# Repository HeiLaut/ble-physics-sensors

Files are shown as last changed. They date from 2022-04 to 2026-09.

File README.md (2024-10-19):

# BLE Sensors for physics class

* [Goal](#goal)
* [Microcontroller and Sensors](#sensors)
   * [Force Sensor](#force)
   * [ToF Distance-Sensor](#tof)
   * [Light Gate](#gate)
   * [Magnetometer](#magnet)
   * [DC Multimeter](#multimeter)
   * [Barometer](#barometer) 

## Goal 

**Easy to use** and affordable sensor boxes for digital data acquisition are suitable for use in physics lessons by students or for teacher demonstrations.

Each box can be assembled for less than 20 €.

Comments and requests for changes to both the 3D files and the Arduino code are welcome.

## Microcontroller and Sensors 

All boxes are equipped with an ESP32, enabling them to communicate via BLE (Bluetooth Low Energy) or a serial connection.

I use the Wemos Lolin32Lite development board because of its availability, the battery connector and the low price.

Most sensors use the I2C interface to communicate with the ESP32.

### Force Sensor 
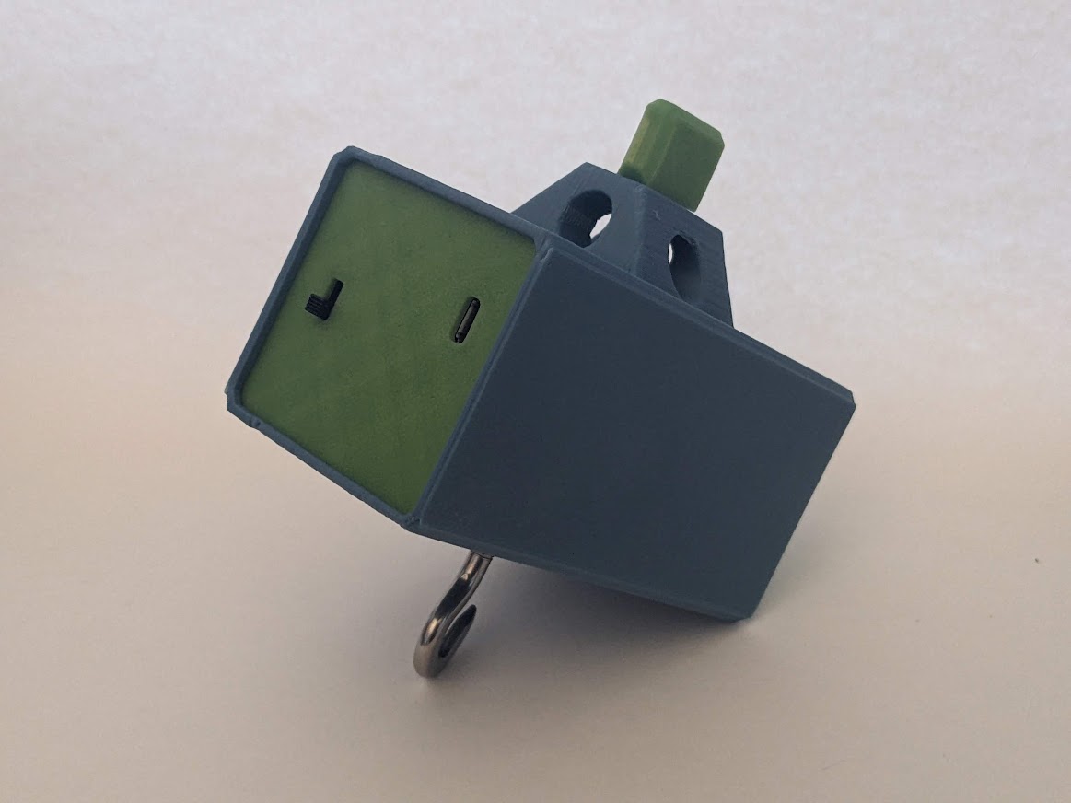
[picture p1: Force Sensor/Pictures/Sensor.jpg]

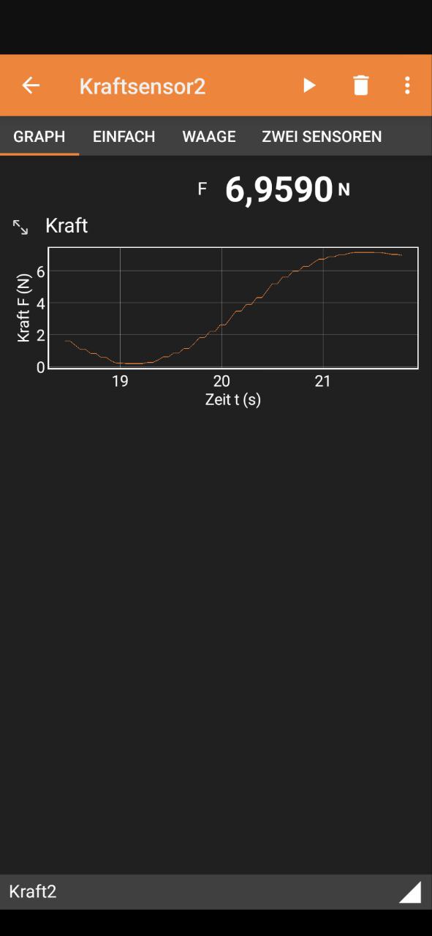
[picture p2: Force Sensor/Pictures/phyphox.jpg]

Sensor:

Load Cell and HX711 amplifier

### ToF Distance-Sensor 
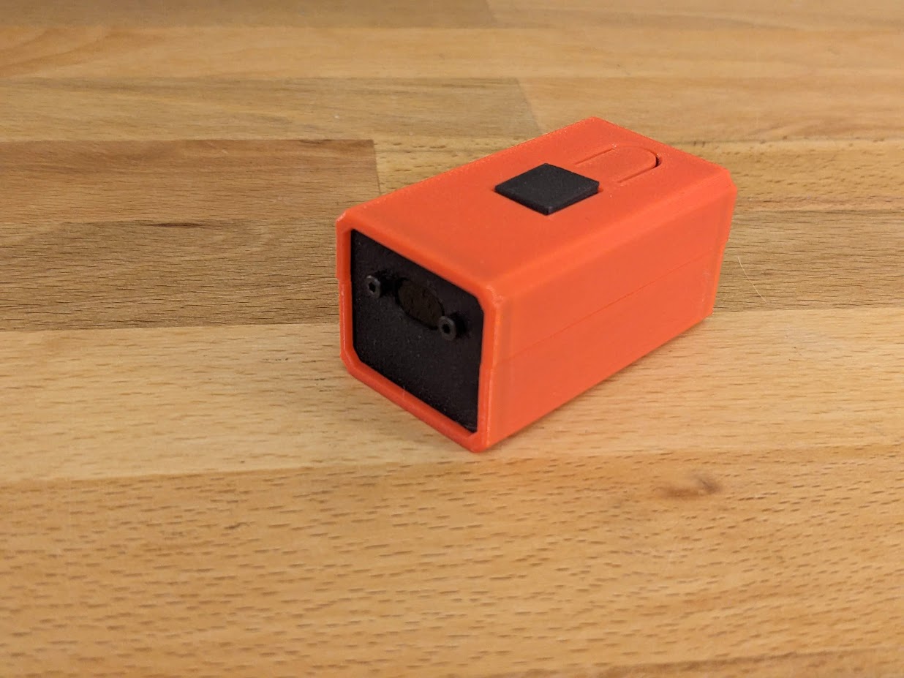
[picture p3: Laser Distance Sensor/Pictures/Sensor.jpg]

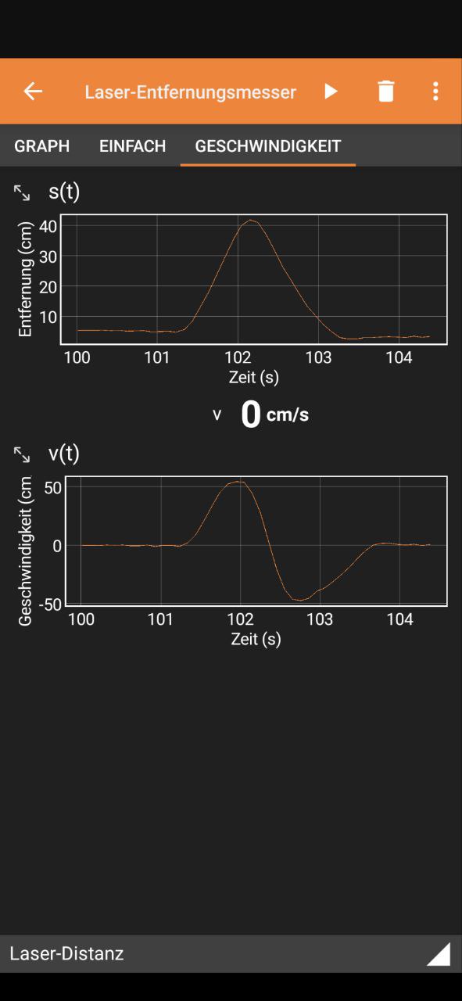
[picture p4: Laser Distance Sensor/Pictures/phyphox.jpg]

Sensor:

VL53L0X

or

VL53L1X

[Assembly instructions see wiki](https://github.com/HeiLaut/ble-physics-sensors/wiki/Laser-Distance)

### Light Gate 

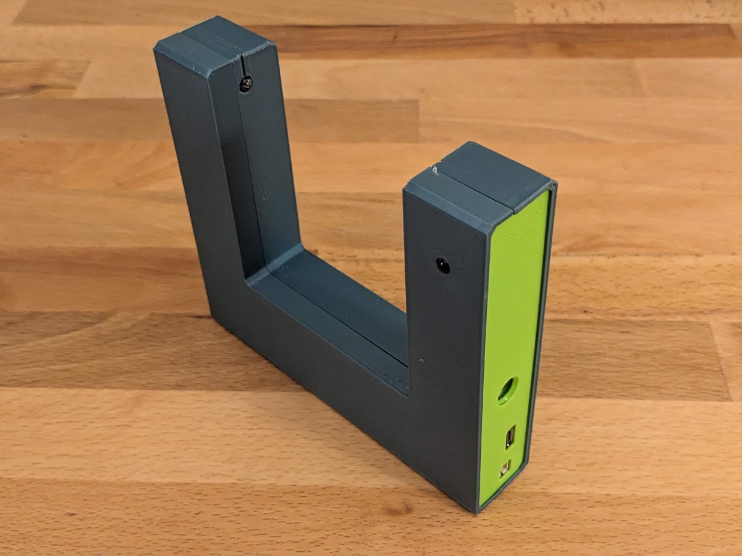
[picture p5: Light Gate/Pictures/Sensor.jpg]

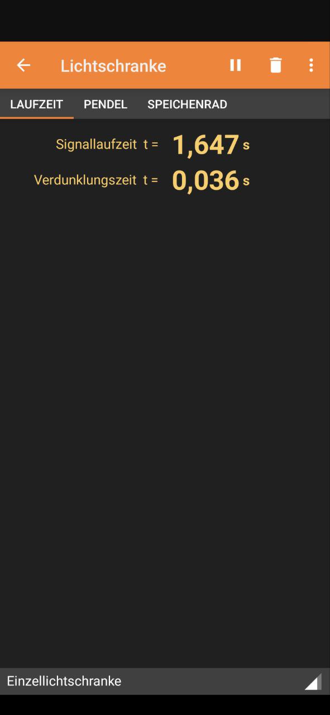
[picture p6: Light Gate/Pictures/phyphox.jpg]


Sensor:

Adafruit Break Beam Sensor 

or (cheaper)

modified lightgate/speed-sensor with LM393

### Magnetometer 
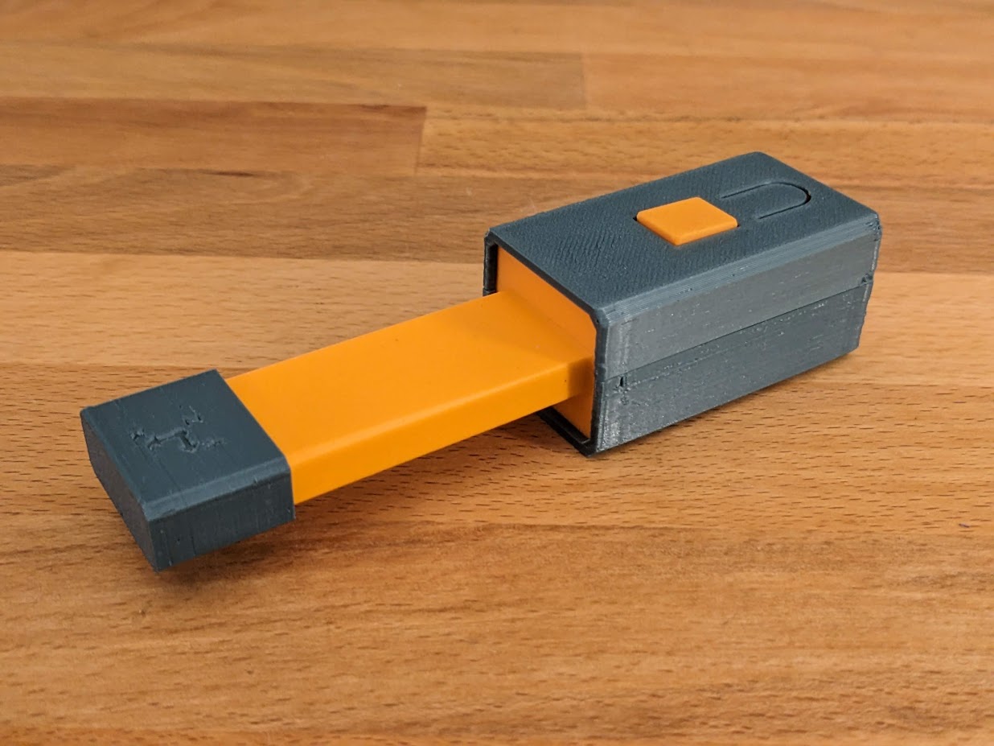
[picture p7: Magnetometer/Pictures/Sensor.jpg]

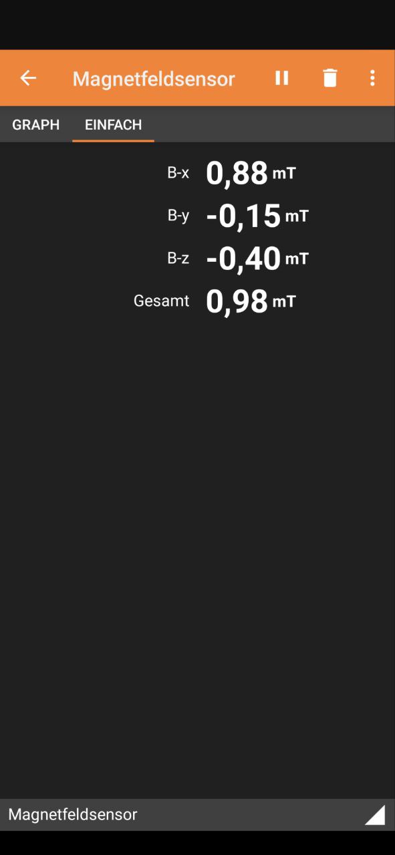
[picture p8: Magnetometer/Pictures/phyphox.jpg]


Sensor:

LIS2MDL

or

MLX90393

or

(Gy-271) low range 

### DC Multimeter 

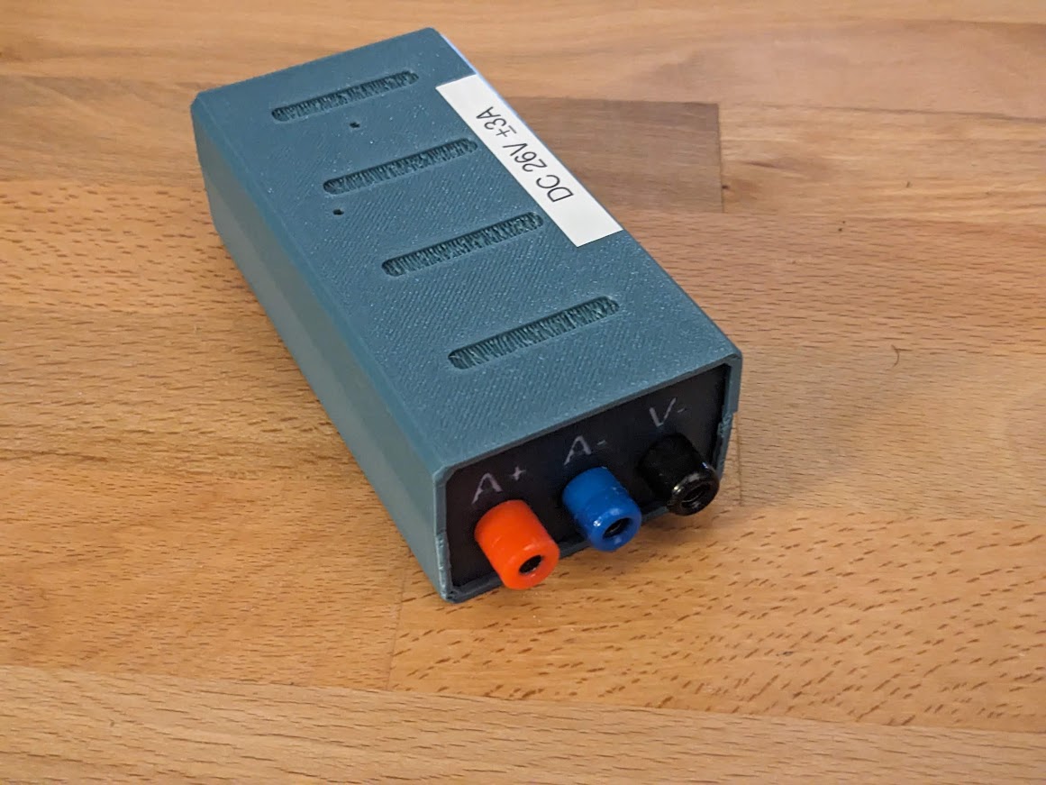
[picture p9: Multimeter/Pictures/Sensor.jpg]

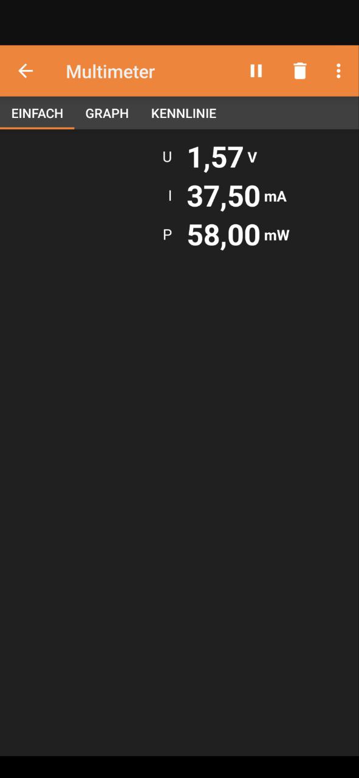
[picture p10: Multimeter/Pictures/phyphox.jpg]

Sensor:

INA219

and (optional)

ADS1115

Example Videos:

Diode characteristic https://youtu.be/DQ5L0hsJfBA

Resistor characteristic https://youtu.be/PSxBtcULFwU

Charge and discharge of a capacitor https://youtube.com/shorts/HkM0g7PQ94s?feature=share

### Barometer 
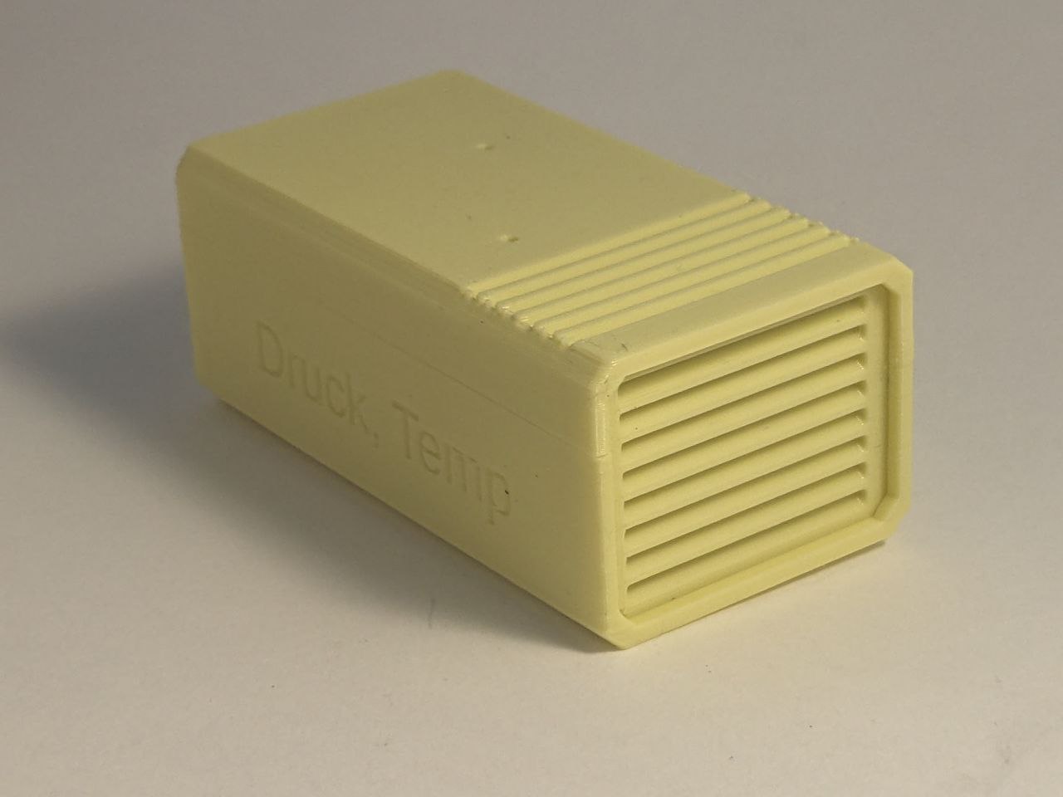
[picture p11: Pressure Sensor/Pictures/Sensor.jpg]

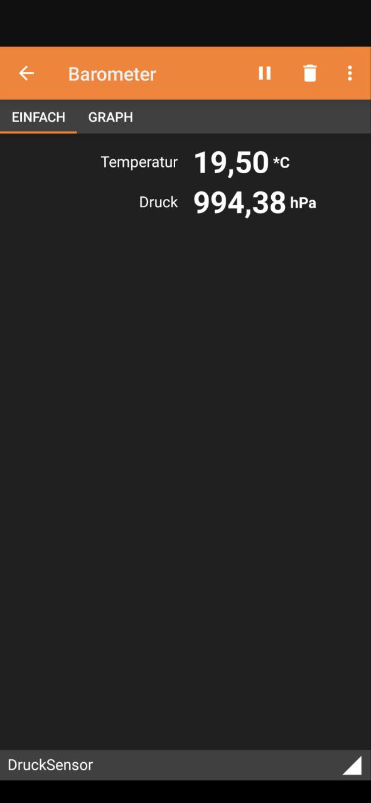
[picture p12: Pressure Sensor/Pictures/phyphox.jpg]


BMP180 Barometer and Thermometer module.

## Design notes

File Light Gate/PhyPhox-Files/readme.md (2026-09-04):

If you use the Arduino sketch, light_gate_qr you must load this experiment to phyphox ether by sharing the phyphox-file or by scanning the QR code.

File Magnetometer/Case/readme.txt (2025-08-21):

This is a case for a Lolin32 Lite and various magnetic field sensor modules.
For all sensors, you need to print:

Bottom_Case_Lolin32Lite.stl
Top_Case_Lolin32Lite.stl
Backplate.stl

Then, you can choose from different sensors.
For each sensor, you need to print:

..._sensor.stl
..._cap.stl

you can also choose the build plate for the LIS2MDL and the MLX90393

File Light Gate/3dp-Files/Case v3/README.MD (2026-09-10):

if you use a break beam sensor from aliexpress, select the break_beam_sensor_version of from the stl

if you have single IR-Emitter and IR-Receiver LEDs by using an IR-Sensor use th 00_BUILD_PLATE.stl

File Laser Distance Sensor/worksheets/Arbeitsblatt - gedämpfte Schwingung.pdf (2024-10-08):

# Gedämpte Schwingung

## Aufgabe

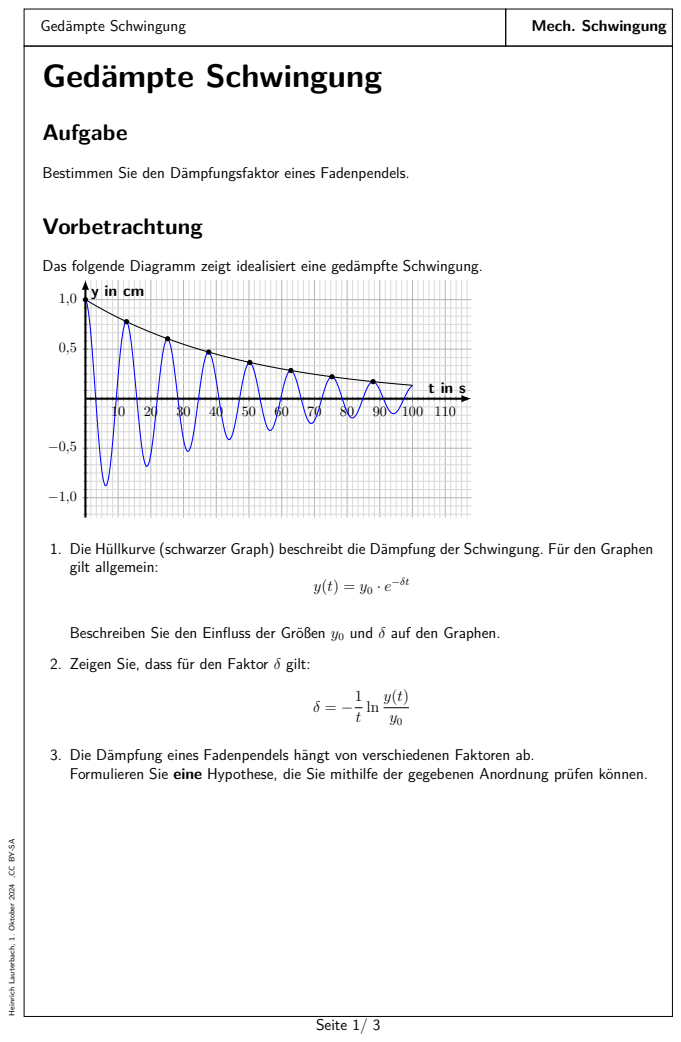
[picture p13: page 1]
Gedämpte Schwingung; Mech. Schwingung; Vorbetrachtung

Bestimmen Sie den Dämpfungsfaktor eines Fadenpendels.

Das folgende Diagramm zeigt idealisiert eine gedämpfte Schwingung.

1. Die Hüllkurve (schwarzer Graph) beschreibt die Dämpfung der Schwingung. Für den Graphen
gilt allgemein:

Beschreiben Sie den Einfluss der Größen y0 und δ auf den Graphen.

2. Zeigen Sie, dass für den Faktor δ gilt:

3. Die Dämpfung eines Fadenpendels hängt von verschiedenen Faktoren ab.
Formulieren Sie eine Hypothese, die Sie mithilfe der gegebenen Anordnung prüfen können.

Heinrich Lauterbach, 1. Oktober 2024 ,CC BY-SA

Heinrich Lauterbach, 1. Oktober 2024 ,CC BY-SA

### Durchführung

1. Hängen Sie das Pendel in Ruhelage auf und positionieren Sie den ToF-Sensor auf Höhe des Pendels.

Versuchsaufbau

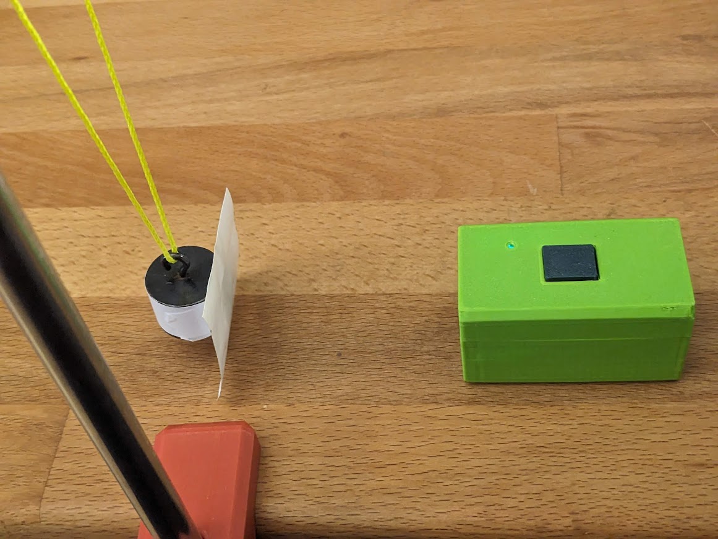
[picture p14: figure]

2. Stellen Sie mithilfe des Tasters auf dem Sensor den Offset ein, sodass der Punkt der Ruhelage auf 0 gesetzt wird.
3. Lenken Sie das Pendel um einen kleinen Winkel aus und starten Sie die Messung mit phyphox.
4. Speichern Sie die Messung auf Ihrem Gerät. (Öffnen Sie das Menü hinter den drei Punkten und klicken Sie auf Zustand speichern.)
5. Wiederholen Sie die Messung, variieren Sie vorher eine Größe entsprechend Ihrer Hypothese.

### Auswertung

1. Entnehmen Sie aus den y(t)-Diagrammen in phyphox jeweils mindestens fünf Amplituden in Abhängigkeit von der Zeit. Vergrößern Sie dazu das s(t)-Diagramm und wählen Sie mithilfe des Cursors die entsprechenden Amplituden aus.
Da die Zeit nicht bei 0 s anfängt, ziehen Sie jeweils den Startwert der Zeit von Ihren abgelesenen Werten ab, sodass die erste Auslenkung bei t = 0 ist.
2. Ermitteln Sie mithilfe der Messwerte die Dämpfungsfaktoren δ der jeweiligen Schwingung.
3. Überprüfen Sie unter Beachtung möglicher aufgetretener Messunsicherheiten Ihre Hypothese.

Heinrich Lauterbach, 1. Oktober 2024 ,CC BY-SA

## Hinweise und Erwartung

Beispielgraph

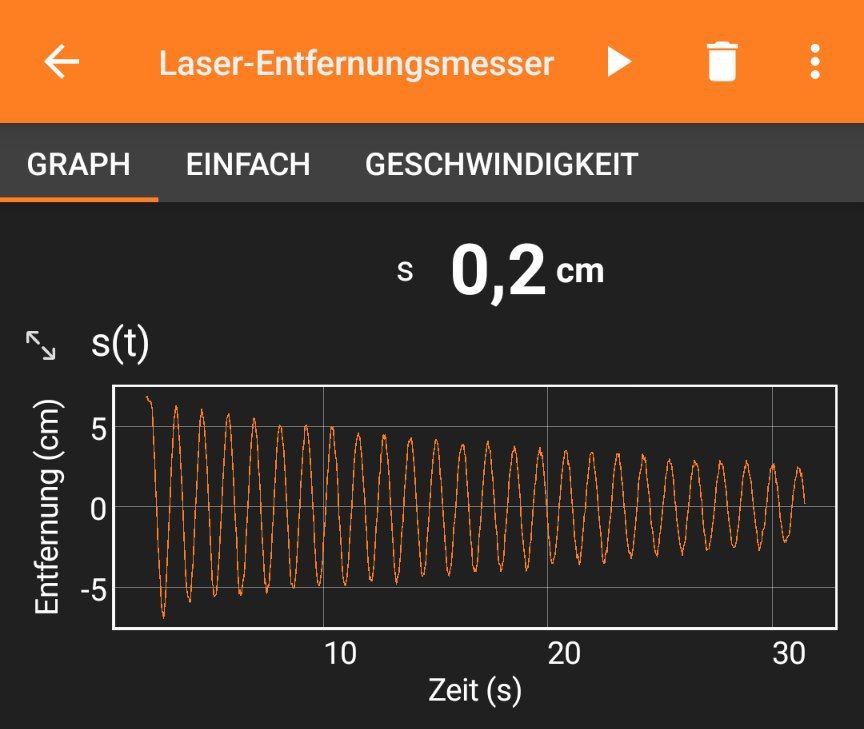
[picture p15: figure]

Beispielmesswerte in unterschiedlichen Abständen
t in s | ti
| in s | y in cm | δ
2,90 | 0 | 6,9 | –
6,33 | 3,43 | 5,5 | 0,066
9,82 | 6,92 | 4,9 | 0,049
14,41 | 11,51 | 4,3 | 0,041
23,71 | 20,81 | 3,2 | 0,037
30,52 | 27,62 | 2,2 | 0,041

δ = 0, 047

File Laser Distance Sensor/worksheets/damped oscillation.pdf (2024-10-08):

# Damped Oscillation

## Task

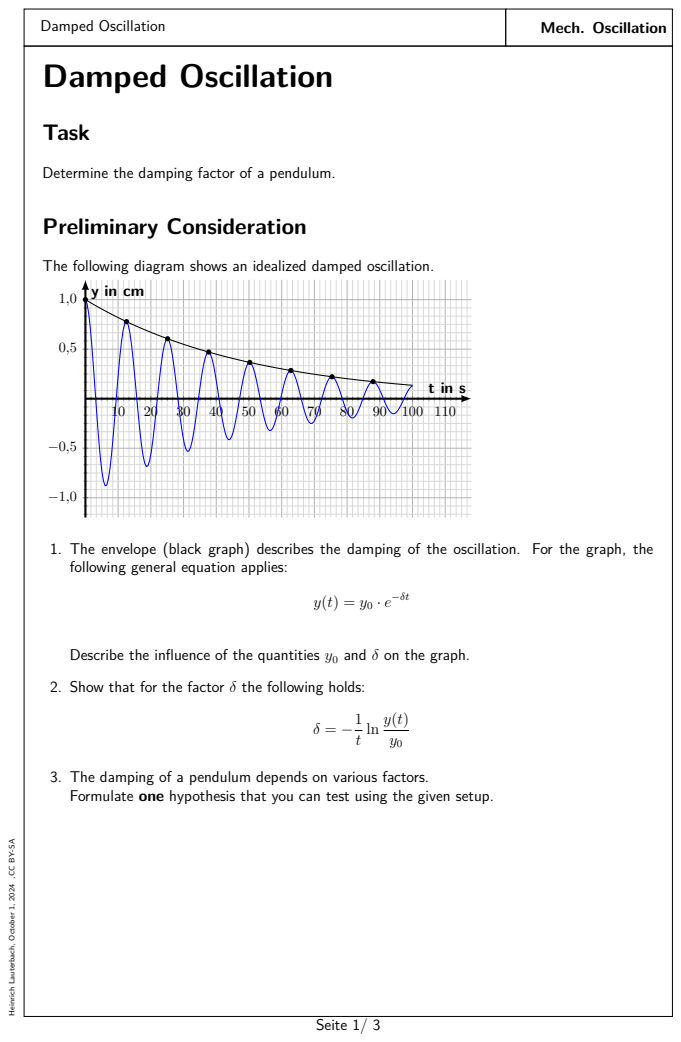
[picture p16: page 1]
Damped Oscillation; Mech. Oscillation; Preliminary Consideration

Determine the damping factor of a pendulum.

The following diagram shows an idealized damped oscillation.

1. The envelope (black graph) describes the damping of the oscillation. For the graph, the
following general equation applies:

Describe the influence of the quantities y0 and δ on the graph.

2. Show that for the factor δ the following holds:

3. The damping of a pendulum depends on various factors.
Formulate one hypothesis that you can test using the given setup.

Heinrich Lauterbach, October 1, 2024 ,CC BY-SA

Heinrich Lauterbach, October 1, 2024 ,CC BY-SA

### Procedure

1. Hang the pendulum in its rest position and position the ToF sensor at the height of the pendulum.

Experimental Setup


2. Use the button on the sensor to set the offset so that the point of rest is set to 0.
3. Displace the pendulum by a small angle and start the measurement with phyphox.
4. Save the measurement on your device. (Open the menu behind the three dots and click on Save State.)
5. Repeat the measurement, varying one parameter according to your hypothesis.

### Evaluation

1. Extract at least five amplitudes as a function of time from the y(t) diagrams in phyphox. To do this, enlarge the s(t) diagram and use the cursor to select the corresponding amplitudes. Since the time does not start at 0 s, subtract the start value of the time from your read values so that the first displacement is at t = 0.
2. Determine the damping factors δ of the respective oscillation using the measured values.
3. Verify your hypothesis, considering possible measurement uncertainties.

Heinrich Lauterbach, October 1, 2024 ,CC BY-SA

## Notes and Expectations

Example Graph


Example Measurements at Different Intervals
t in s | ti
| in s | y in cm | δ
2.90 | 0 | 6.9 | –
6.33 | 3.43 | 5.5 | 0.066
9.82 | 6.92 | 4.9 | 0.049
14.41 | 11.51 | 4.3 | 0.041
23.71 | 20.81 | 3.2 | 0.037
30.52 | 27.62 | 2.2 | 0.041

δ = 0.047

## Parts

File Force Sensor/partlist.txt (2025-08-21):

esp32 lolin lite
1kg load cell with hx711

2 m4x20 screws
2 m4 nuts
1 m5 hook
2 m5x14 screws
12 x 12 x 7.3 mm tactile push button

optional:
SS-12F15 on/off-switch
lipo battery

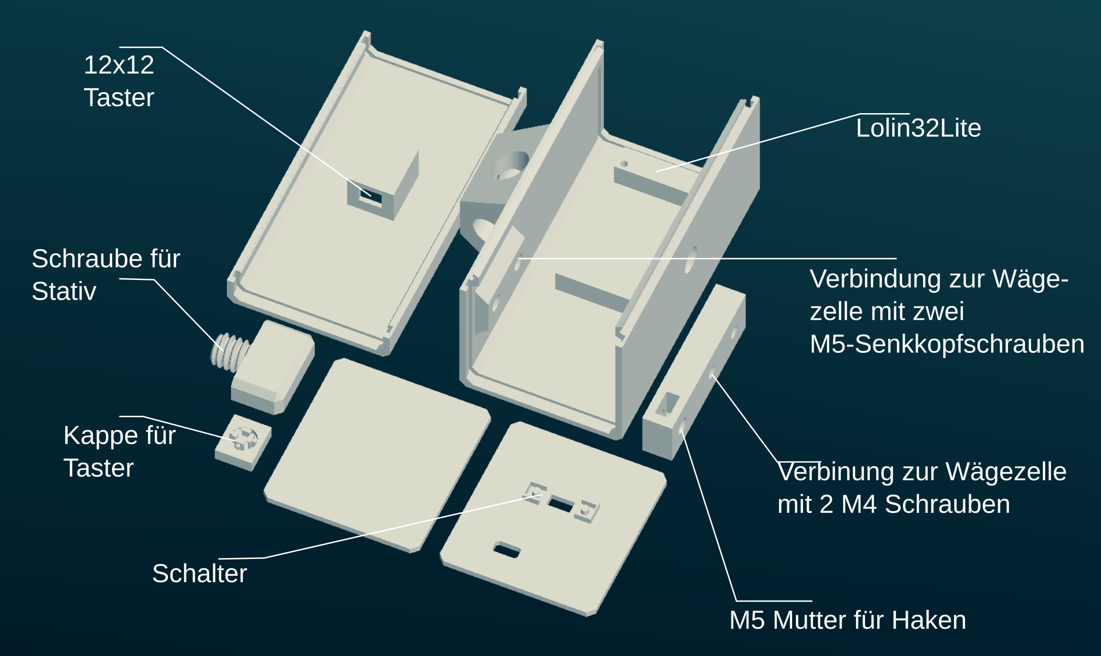
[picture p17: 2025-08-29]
Force Sensor/Pictures/parts_de.png

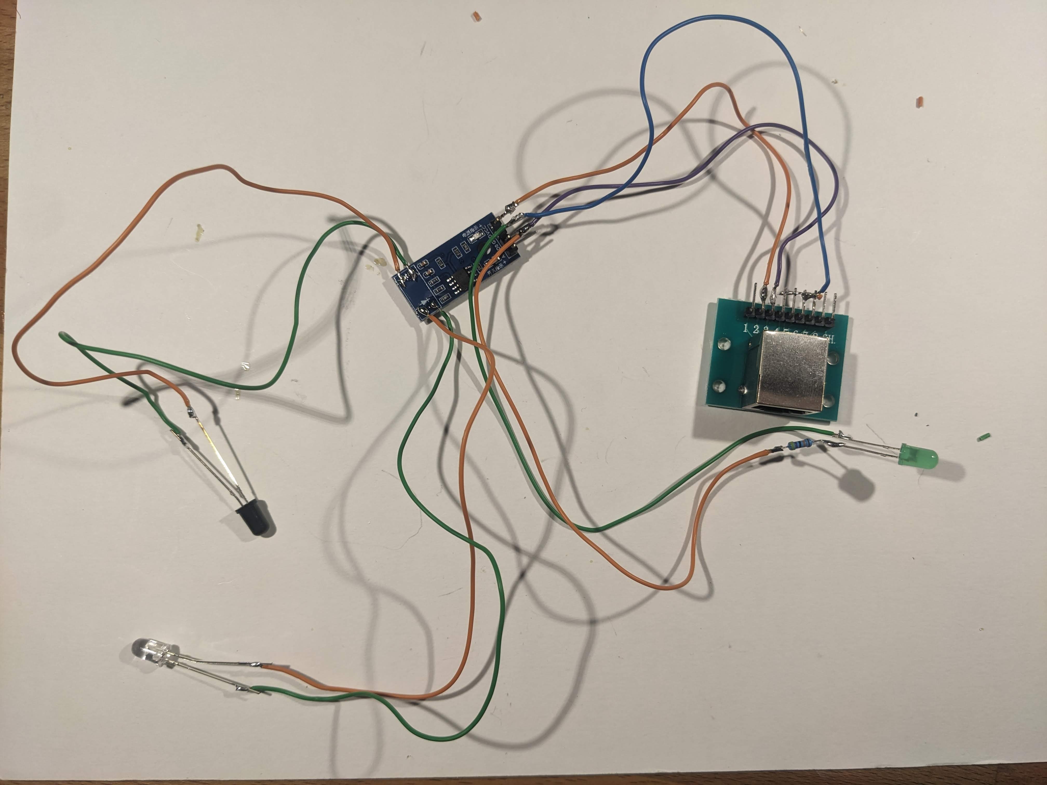
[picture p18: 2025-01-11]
Light Gate/Pictures/Instructions/parts_2nd_lightgate.jpg

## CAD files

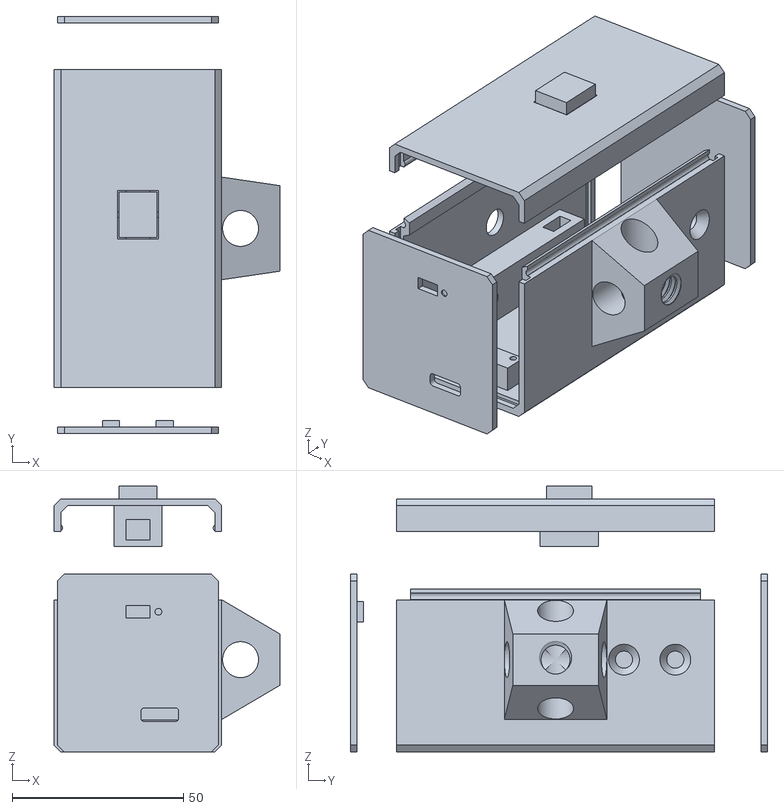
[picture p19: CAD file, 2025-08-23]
Force Sensor/3dp-Files/case_assembly.stl
66.0 x 122.0 x 77.8

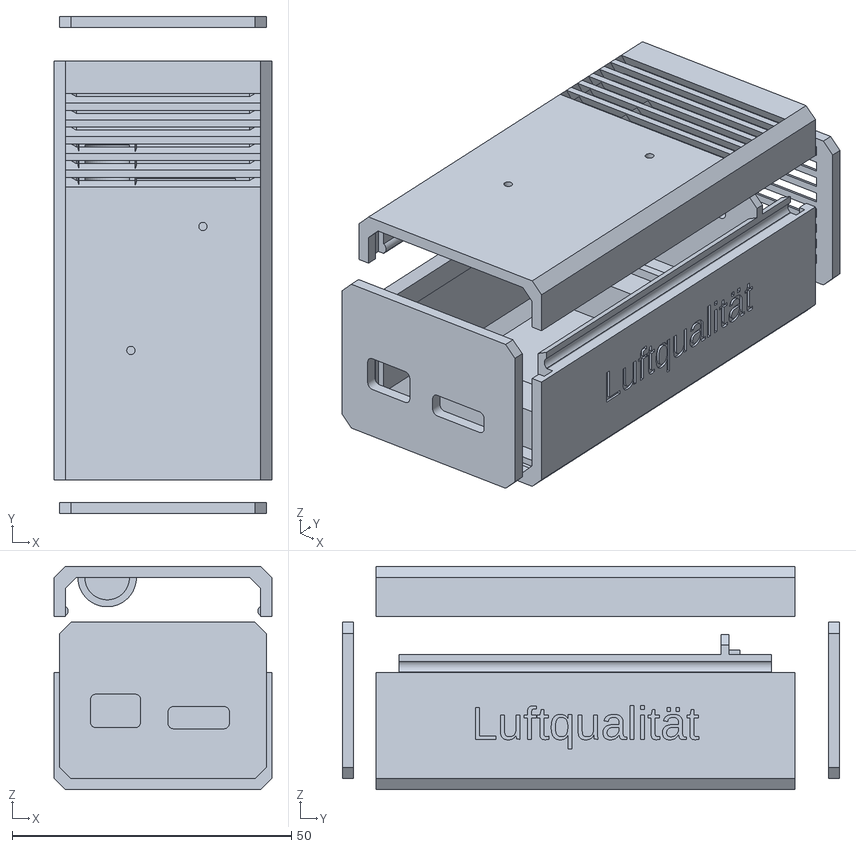
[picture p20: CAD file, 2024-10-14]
Airquality/3dp/AirQualityCase.stl
39.0 x 89.0 x 40.0

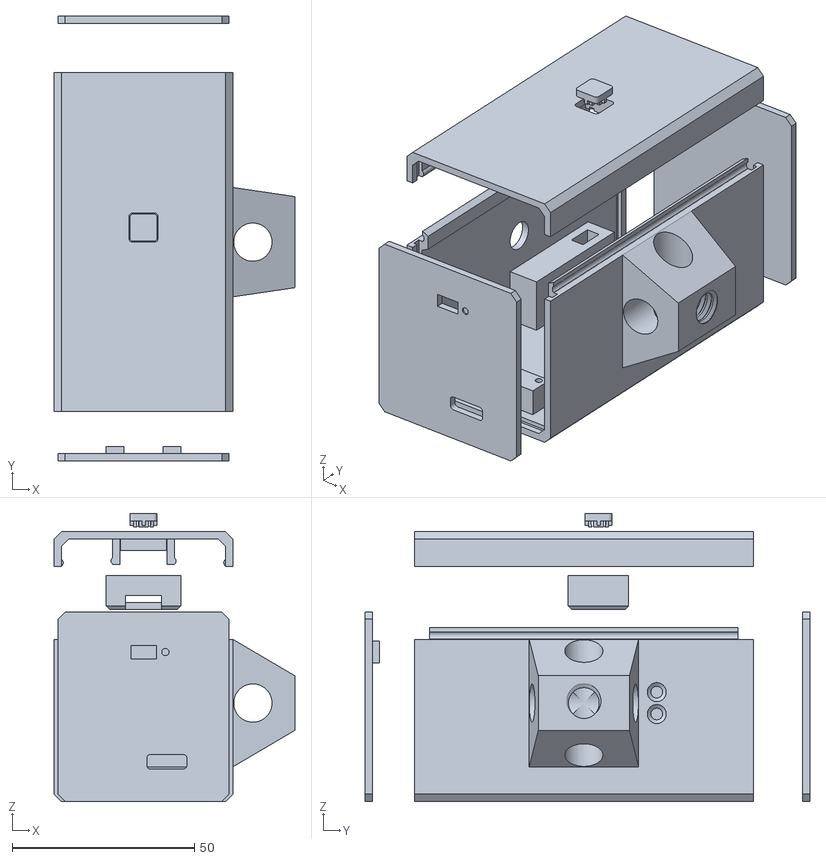
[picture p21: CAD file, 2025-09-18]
Force Sensor/3dp-Files/case_v5_100g_LoadCell.stl
66.0 x 122.0 x 79.0

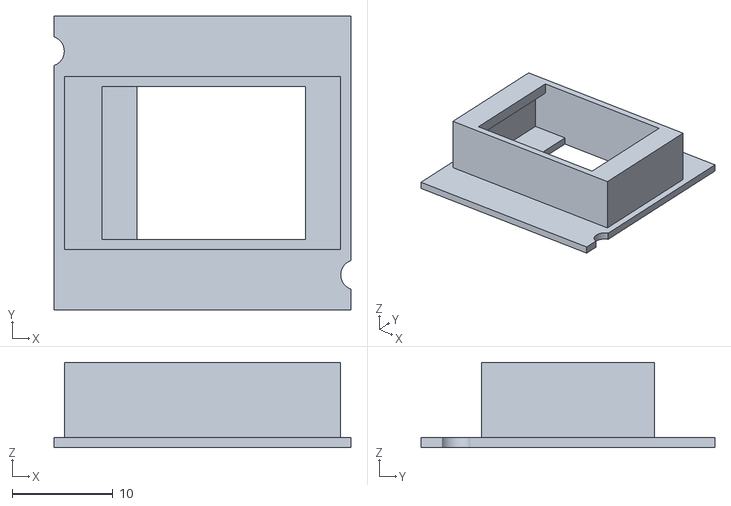
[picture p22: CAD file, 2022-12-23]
Force Sensor/3dp-Files/parts/rj45-blende-edit.stl
29.5 x 29.2 x 8.50

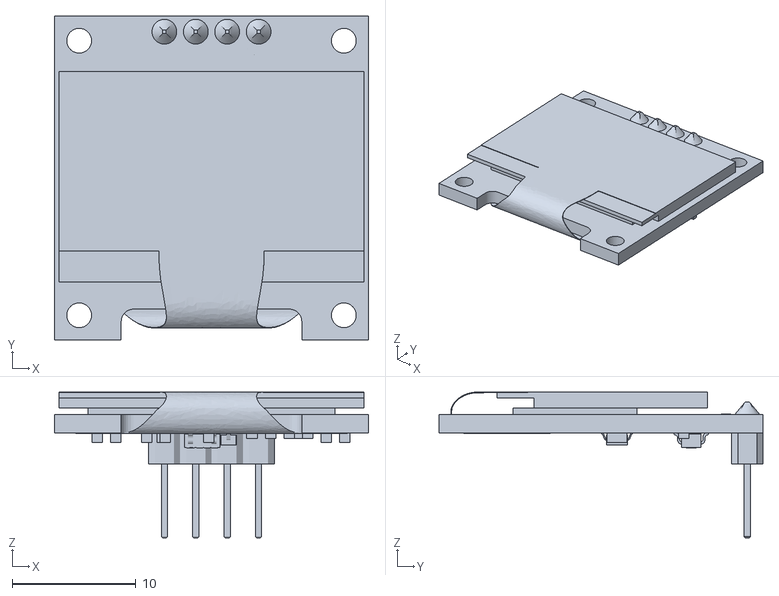
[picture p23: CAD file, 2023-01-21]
Infrared Reflection Sensor/3dp-Files/parts/OLED.stl
25.4 x 26.2 x 11.8

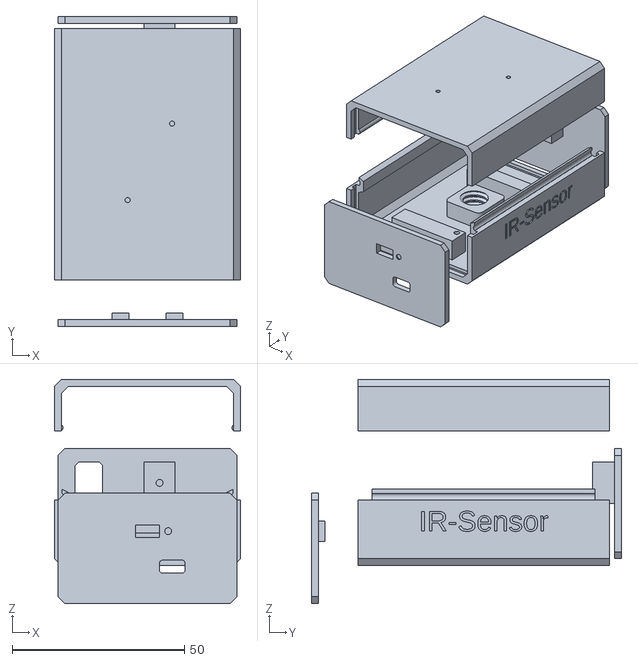
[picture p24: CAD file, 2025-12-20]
Infrared Reflection Sensor/3dp-Files/TR5000Case.stl
54.0 x 90.0 x 65.0

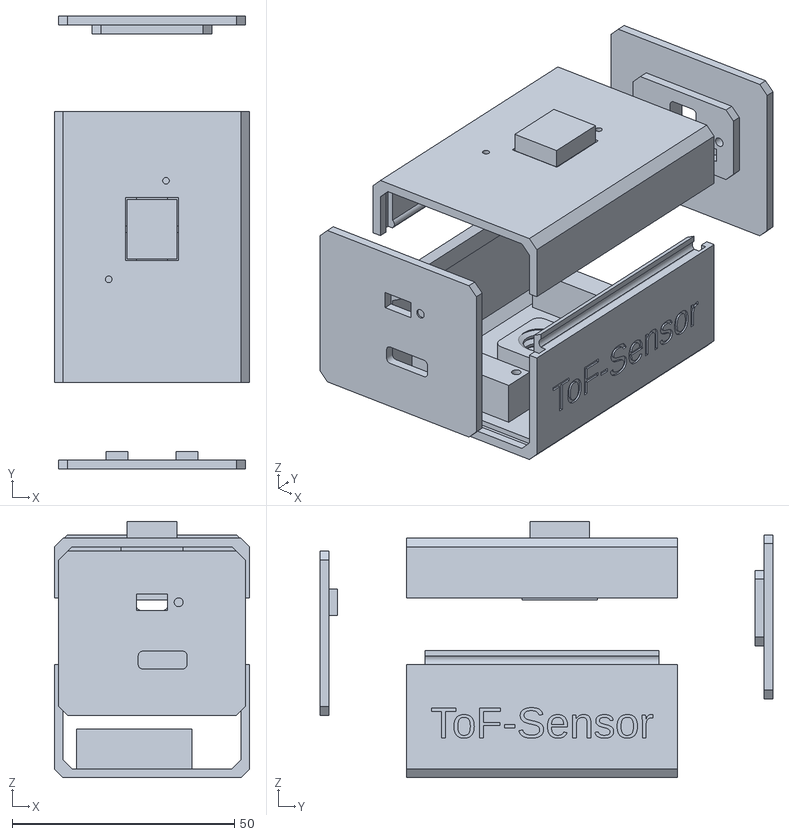
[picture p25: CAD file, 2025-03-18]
Laser Distance Sensor/3dp-Files/Case v2/vl53l0x_case2.stl
44.0 x 102.0 x 57.8

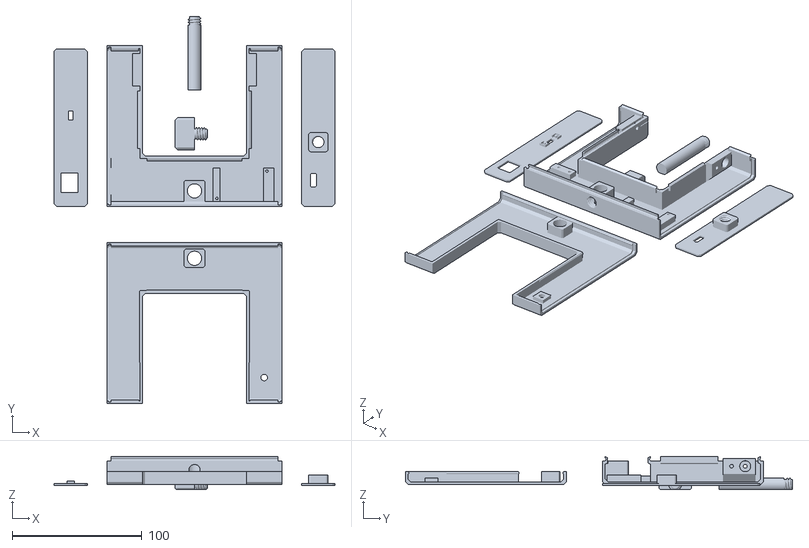
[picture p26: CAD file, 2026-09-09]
Light Gate/3dp-Files/Case v3/break_beam_sensor_version_build_plate.stl
216.6 x 298.5 x 25.5

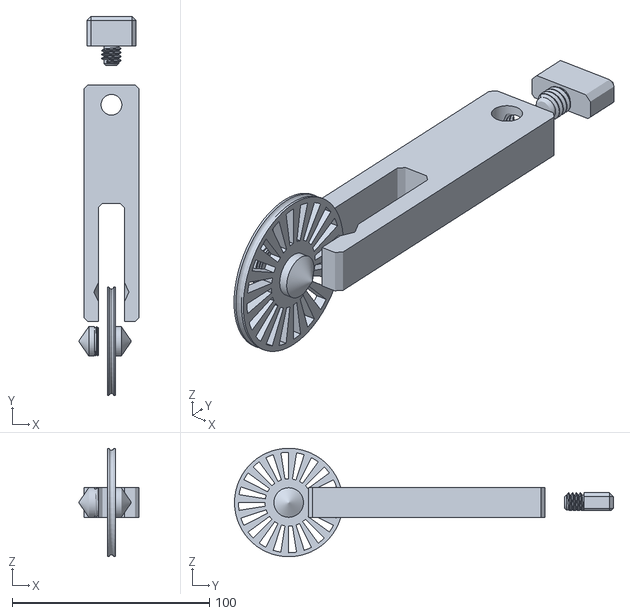
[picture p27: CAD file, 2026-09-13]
Light Gate/3dp-Files/Case v3/Encoder-Wheel/Encoder_Wheel_3d_only.stl
30.5 x 192.3 x 55.0

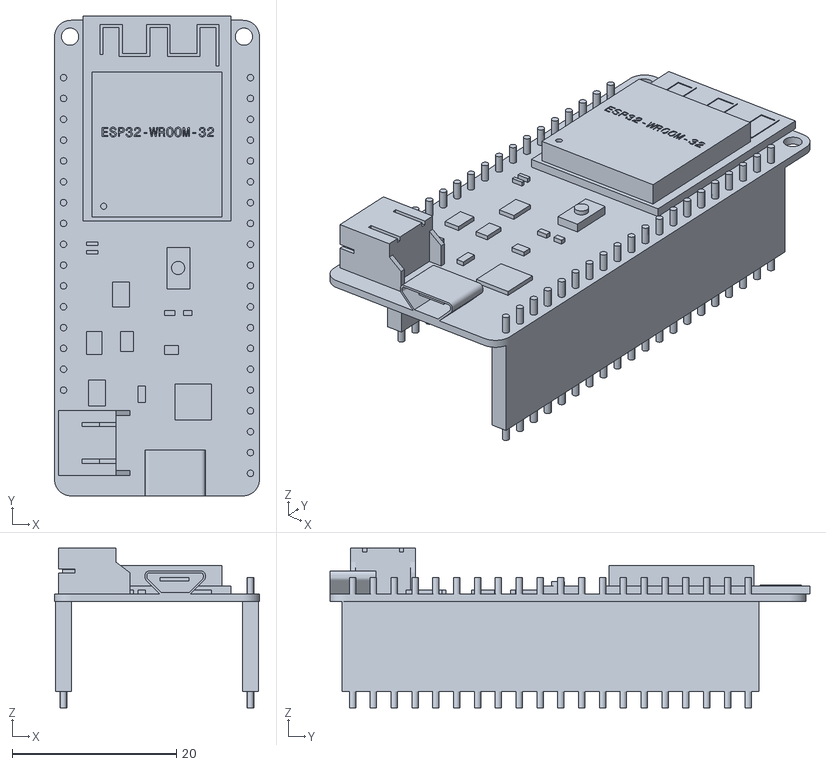
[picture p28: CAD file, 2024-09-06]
Light Gate/3dp-Files/Case v3/parts/Wemos-Lolin32.stl
25.0 x 58.5 x 19.5

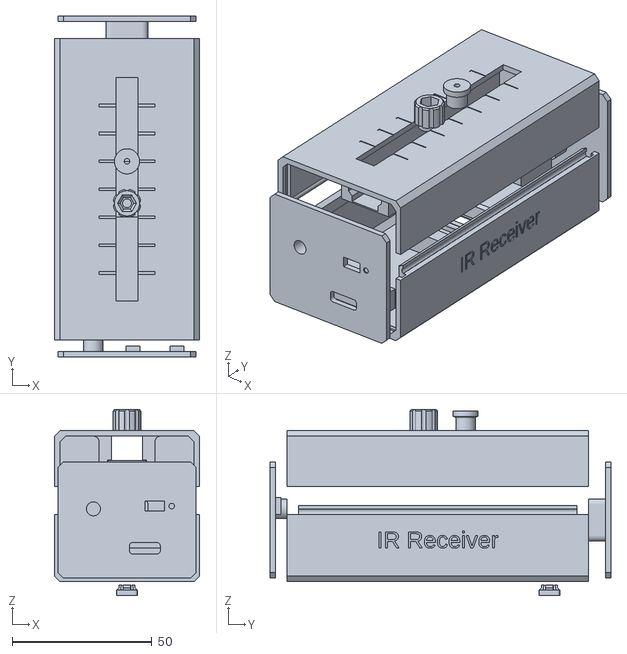
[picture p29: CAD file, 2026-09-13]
Light Gate/3dp-Files/receiver emitter seperate/Receiver_case_all_parts.stl
52.0 x 122.0 x 66.5

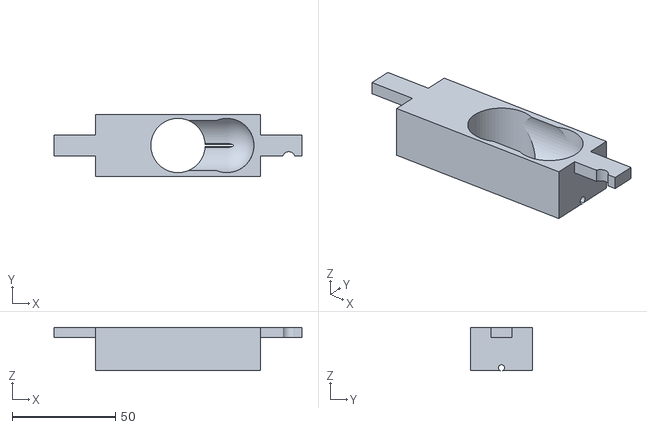
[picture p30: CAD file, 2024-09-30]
Light Gate/3dp-Files/Startvorrichtung/Kugelstarter25_3.stl
120.0 x 30.0 x 21.0

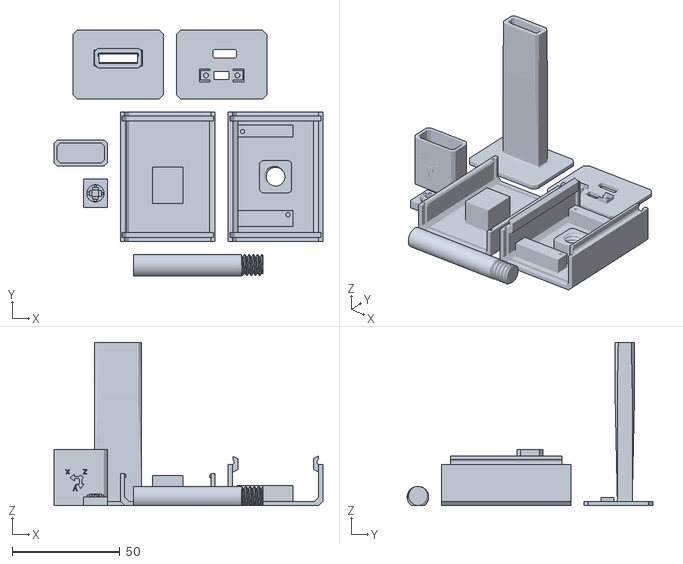
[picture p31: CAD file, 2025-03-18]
Magnetometer/Case/lis2mdl_build_plate.stl
124.8 x 114.0 x 75.8

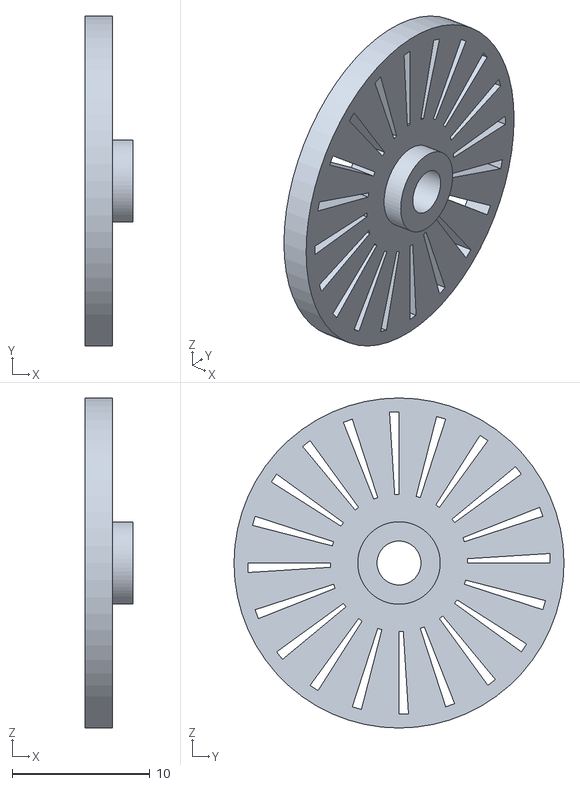
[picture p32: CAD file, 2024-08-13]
Messwagen/3dp-Files/Encoder_Wheel.stl
3.50 x 24.0 x 24.0

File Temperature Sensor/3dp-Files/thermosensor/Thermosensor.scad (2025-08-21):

include <BOSL/constants.scad>
use <BOSL/transforms.scad>
use <BOSL/shapes.scad>
use <BOSL/masks.scad>

$fn = 60;
x= 52;
z = 23;
y = 30+28;



module esp(){
   color("red")translate([1.5,42.5,0])rotate([180,0,-90])import("/parts/lolin32_lite.stl");
}

module connectorboard(){
   xB = 38;
   yB = 30;
   zB = 1.5;
   cuboid([xB,yB,zB]);
   color("blue")translate([0,yB/2-5,zB-0.5]){
   translate([xB/2-8.5,0,0])import("/parts/jst.stl");
   translate([xB/2-26,0,0])import("/parts/jst.stl");
   }


}
module parts(){
   translate([-38/2,30/2+1,0.75])connectorboard();
   translate([0.5,-25,0])rotate([0,1,0])rotate([0,0,90])esp();
}

module case(){
   module screwshaft(){
        difference(){
            cylinder(d=4,h=z-3);
            up(15)cylinder(d=2,h=z);
            up(5)rotate([0,-50,0])cuboid([20,10,10]);
        }
    }
    for(i=[ [-x/2+1.7,-y/2+1.7,-z/2+3.7],
            [-x/2+1.7,y/2-1.7,-z/2+3.7]]){
        translate(i)screwshaft();
    }
    mirror([1,0,0])for(i=[ [-x/2+1.7,-y/2+1.7,-z/2+3.7],
            [-x/2+1.7,y/2-1.7,-z/2+3.7]]){
        translate(i)screwshaft();
    }
   module lolinmount(){
       d = 2;
       h = 6.5;
       translate([-x/2+5,-y/2+13.7,-z/2+h/2])difference(){
            cuboid([5,26,h]);
            translate([-0.75,1-11.2,-2])cylinder(d=d,h=h);
      }
      translate([x/2-8.5,-y/2+13.7,-z/2+h/2])difference(){
            cuboid([5,26,h]);
            translate([-0.75,11,-2])cylinder(d=d,h=h);
      }
   }
   module conmount(){
      h = 6;
      translate([x/2-35/2-2,25/2,-z/2+h/2])difference(){
         cuboid([37,25,h]);
         translate([0,3,-0.2])cuboid([35-6,25,h+1]);
      }
     
   }
       
        
   difference(){
      cuboid([x+3,y+3,z+1.5],chamfer =2,edges = EDGES_Z_ALL);
      translate([0,0,0.75])cuboid([x,y,z+1],chamfer =2,edges = EDGES_Z_ALL);
      //JST
      translate([16.54,y/2+1,-1])cuboid([11,3,8]);
      translate([-1,y/2+1,-1])cuboid([11,3,8]);
      //esp
      translate([x/2+1,-23,-1.5])cuboid([3,10,8.5]);
      translate([x/2+1,-7.5,-2.5])cuboid([3,9,5]);
     }
    translate([0.5,0.5,0])lolinmount();
    conmount();
   }
   
module lid(){
   difference(){
         cuboid([x+3,y+3,1.5],chamfer =2,edges = EDGES_Z_ALL);
       for(i=[ [-x/2+1.7,-y/2+1.7,-z/2+3.7],
            [-x/2+1.7,y/2-1.7,-z/2+3.7]]){
        translate(i)cylinder(d=2,h=z);
    }
    mirror([1,0,0])for(i=[ [-x/2+1.7,-y/2+1.7,-z/2+3.7],
            [-x/2+1.7,y/2-1.7,-z/2+3.7]]){
        translate(i)cylinder(d=2,h=z);
    }
}
}
difference(){
   union(){
      case();
      translate([0,0,z/2+10])lid();
      *translate([x/2-1,-2.5,-5])parts();
   }
   //translate([0,-50,-50])cube([100,100,100]);
}

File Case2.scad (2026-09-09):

/*
  Universal Electronic Case
  
  Version: 0.41 //July 2026
  
  Created by: Heinrich Lauterbach
  License: CC-BY-SA
  This file is licensed under the Creative Commons Attribution-ShareAlike 4.0 International License.
  To view a copy of this license, visit http://creativecommons.org/licenses/by-sa/4.0/
  
  needs BOSL2 library
  download BOSL2 to your libraries folder via: https://github.com/BelfrySCAD/BOSL2
*/





include<BOSL2/std.scad>
include<BOSL2/threading.scad>



$fn = 50;
/*intersection(){
    test();
    translate([0,-30,-10])cuboid([30,20,20]);
    }
*/
module test(){
lolinspace = 5;
z = 30;
x=80;
y=70;
case([x,y,z],part="bottom",explode = 25,rd=2,lolinspace = lolinspace,button = 0,reset = 0, thread = 0,clearance = 0.2,embosstext = "TEST");
*case([x,y,z],part="top",explode = 50,rd=2,lolinspace = lolinspace,button = 1,reset = 0, thread = true,usbC = 1, wall=2,jst = 1,switch=1,charge_view = 1,
   power_view = 1);
*color("red")translate([-11.5,16.5,lolinspace-12])rotate([180,0,-90])import("lolin32_lite.stl");
}
////must be larger than 1.5 mm
module case(
   size = [15,15,15], //size [x,y,z]
   clearance = 0.15, //overall clearance,
   plate_clearance = 0,//makes the plate smaller, if the print of the large parts gets a bit loose, while printing
   wall = 2, //wall thickness
   rd = 2, //chamfer radius
   cutheight = 2, //offset of cutheight
   snap = 2, //width of snap 
   part = "all",//top, bottom, plate
   explode = 0, //show parts seperate
   lolin32lite = true, //lolin32lite mount
   lolinspace = 7.4, //spacing of lolin32lite aboce bottom part
   lolinsnap = 1,
   thread = false, //add thread on bottom part for rod
   button = false,//add buttonhole on top part
   reset = false, //add reset button
   usb = false, //add cutout for micro usb on plate
   usbC = false,//add cutout for usb-c on plate
   jst = false,//add cutout for jst (battery)
   lolinx = 0,//x-offset of lolin32lite
   charge_view = 0,//add hole on top to see charging-LED
   power_view = 0,//add hole on top to see power-LED
   buttonpos = [0,4],//position of button in top part [x,y]
   switch = 0, //mounting for on-off-switch in plate
   switchpos = [0,5],//switch postion [y,z]
   switchrot = 0,//rotation of switch in degree
   embosstext = "",//embosstext on bottom part
   embossrot = [90,0,90],
   embossheight = 0.4,//embossheight means depth
   embosspos = [0,-5]
   )
   {
   x = size[0];
   y = size[1];
   z = size[2];
   embosspos = [x/2+2-0.2,embosspos[0],embosspos[1]];


   ox = x+2*wall;
   oy = y+4*wall;
   oz = z+2*wall;
   // select chamfer OR rounding
   //chamfer = 1;
   //rounding = 1;

   //rd = 2;

   clearance = clearance;

   //overlap of front and back plate into body
   overlap = 1;

   //height of cut between upper and lower half. 0 means in the middle <1 upper half bigger than lower half; >1 lower half bigger than upper half
   //cutheight = snap;

   //snap parts
   d1 = snap;

   if(cutheight>z/2-wall){
      echo("Cuthehgt to large");
   }
   module body(explode = 2,part){
         module both(){
            difference(){
            cuboid([ox,oy,oz],chamfer = rd,except=[FRONT,BACK]);
            cuboid([x,oy+1,z],chamfer = rd,except=[FRONT,BACK]);
            for(i = [-1,1]){
               translate([0,i*(-y/2-wall/2),0])cuboid([x+2*overlap+clearance*2,wall+clearance*2,z+2*overlap+clearance*2],chamfer = rd,except=[FRONT,BACK]);
               }//end for
            }//end difference
            }//end both
            
          //top part of the case
         module upper(){
            difference(){
               both();
               translate([0,0,cutheight])cuboid(x*y,anchor=TOP);
               if(button){
                  translate([buttonpos[0],buttonpos[1],z/2])rotate([180,0,90])buttonCase2("cutout",wall);
                  }
               //reset button
               if(reset){
                  translate([-0.8,-y/2+5,z/2+0.1])difference(){
                     union(){
                        cyl(d=10,h=4);
                        cuboid([10,10,4],anchor=FRONT);
                        }//end union
                       cyl(d=8.5,h=4);
                       cuboid([8.5,10,4],anchor=FRONT);
                     }//end difference
                     translate([-0.8,-y/2+5,z/2-1])union(){
                        cyl(d=10,h=4);
                        cuboid([10,10,4],anchor=FRONT);
                  }//end union
                  //LED-cutouts
                

                  }//end if reset
                  if(charge_view)translate([-5.75+lolinx,-6.8-y/2+52/2,z/2])cyl(d=1.5,h=10);
                  if(power_view)translate([7.15+lolinx,15.4-y/2+52/2,z/2])cyl(d=1.5,h=10);
            }//end difference
            
            //snap connector male
            for(i = [-1,1]){
               translate([i*(-x/2-d1/4),0,cutheight+d1/2])difference(){
                  ycyl(d = d1, h = y-clearance*2);
                  translate([-i*d1/4,0,0])cuboid([3*d1/4,y-clearance*2,d1]);
                  }
               }//end for
            if(button){
               translate([buttonpos[0],buttonpos[1],z/2])rotate([180,0,90]){
               buttonCase2("snap");
               up(10)buttonCase2("cover");
               down(5)buttonCase2("cap");

               }
               }
            if(reset){
                translate([-0.8,-y/2+3.5,z/2+1])cyl(d=3,h=z-lolinspace-2.6,anchor=TOP);

            }
         }//end uppercase
         
         //lower part of the case
         module lower(){
            difference(){
               both();
               translate([0,0,cutheight])cuboid(x*y,anchor=BOTTOM);
               if(button){
                  #translate([buttonpos[0],buttonpos[1],-z/2])rotate([0,0,90])buttonCase2("cutout",wall);
                  }
               if(thread){
                  translate([0,0,-z/2])cuboid([13,13,15],rounding=2,except=[TOP,BOTTOM]);
               }//end if thread
               //embosstext
               if(embosstext!="")translate(embosspos)rotate(embossrot)text3d(embosstext,size=6,h=embossheight,anchor=CENTER);
            }//end difference
            //snap connector female
            for(i=[-1,1]){
               difference(){
                  translate([i*(x/2),0,cutheight+d1/8])rotate([0,i*90,0])prismoid(size1=[d1*2,y-clearance*2], size2=[d1*3,y-clearance*2], h=d1,anchor=TOP);
                  translate([i*(x/2+d1/4),0,cutheight+d1/2])ycyl(d = d1+clearance*2, h = y-clearance*2);
                  translate([i*(x/2-clearance/2),0,cutheight])cuboid([clearance,y,d1*4/2],anchor = BOTTOM);
                  }//end difference
               }//end for
               if(button){
               translate([buttonpos[0],buttonpos[1],-z/2])rotate([0,0,90]){
               buttonCase2("snap");
               up(10)buttonCase2("cover");
               down(5)buttonCase2("cap");

               }
               }
              if(lolin32lite){
                  translate([lolinx,-(y-52)/2,0])difference(){
                     union(){
                        translate([0,-23,-z/2])cuboid([25,7.3,lolinspace],anchor = BOTTOM+FRONT);
                        translate([0,24,-z/2])cuboid([26,5.5,lolinspace],anchor = BOTTOM+BACK);
                        if(lolinsnap){
                            for(i=[-1,1])translate([i*13.3,-24.5,-z/2])cuboid([1.2,10,lolinspace+1.7],anchor =BOTTOM+FRONT)
                                attach(TOP)ycyl(d=2,h=10 );
                        }//end if lolinsnap
                     }//end union
                  translate([10.8,-17.6,-z/2])cyl(d=2,h=lolinspace+1,anchor = BOTTOM);
                  translate([-10.3,21,-z/2])cyl(d=2,h=lolinspace+1,anchor = BOTTOM);
                 }//end difference
               }//end if lolin32lite
               
               //threadmount
               if(thread){
                  translate([0,0,-z/2-wall])rodmount();
               }//end if thread
         }//end lowercase
         if(part == "upper"){
            up(explode/2)upper();
            }else{
            down(explode/2)lower();
            }
         
         
   }//end body
   module frontplate(plate_clearance=plate_clearance){
      cuboid([x+2*overlap-plate_clearance,wall,z+2*overlap-plate_clearance],chamfer = rd,except=[FRONT,BACK]);
      }//end frontplate



   if(part == "all"){
      body(explode,"upper");
      body(explode,"lower");
      fwd(explode+y/2+wall/2)frontplate();
      back(explode)translate([0,-1*(-y/2-wall/2),0])frontaplate();
      }
   if(part == "top"){
      down(z/2)body(explode,"upper");

   }
   if(part == "bottom"){
      up(z/2)body(explode,"lower");
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

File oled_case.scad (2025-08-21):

module oledCase(PART = "cutout"){
    if(PART == "cutout")cutout();
    if(PART == "snap")snap();
    if(PART == "cover")cover();
    $fn = 60;
    wall = 2;
    PARTS = 0;
    CUT = 0;
    FACE = FRONT;
    tol = 0.2;
    //OLED BOARD
    boardSize = [39,12,3.5];
    //OLED DISPLAY
    disSize = [25,8];

    module board(){
        color("red"){
            cuboid(boardSize,anchor= BOTTOM);
            translate([boardSize[0]/2-3/2-0.2,0,boardSize[2]])cuboid([3,10,8.5],anchor=BOTTOM);
            }
        
        }


    module cutout(){
        union(){
            //cuboid([50,30,wall],chamfer = 4, except=[TOP,BOTTOM],anchor=TOP);
            cuboid([disSize[0],disSize[1],wall+1],rounding = 1, except=[TOP,BOTTOM],anchor=TOP);
            #cuboid([disSize[0],disSize[1],wall],chamfer = -1, edges=[BOTTOM],anchor=TOP);
            }
            }
    
    
    module snap(){       
        for(i=[-1,1]){
            fwd(i*(boardSize[1]/2+1+tol)){
                cuboid([boardSize[0],2,boardSize[2]],anchor=BOTTOM);
                translate([0,-i/2,boardSize[2]-1])xcyl(d = 2,h = boardSize[0]);
                }
            }
    }

    module cover(){
        difference(){
            cuboid([boardSize[0]+2*wall+tol*2,boardSize[1]+2*wall+4,boardSize[2]+tol*2+wall],anchor=BOTTOM,chamfer=1,edges=TOP);
            cuboid([boardSize[0]+tol*3,boardSize[1]+2*wall+3*tol,boardSize[2]+tol*2],anchor=BOTTOM);
            for(i=[-1,1]){
                translate([0,-i*(boardSize[1]/2+1+tol+1/2),boardSize[2]-1-tol/2])xcyl(d = 2+tol,h = boardSize[0]);
                 translate([boardSize[0]/2-3/2-0.2,0,boardSize[2]])cuboid([5,12,8.5],anchor=BOTTOM);
                
            }
    }
    }
//    difference(){
//        union(){
//            baseplate();
//            up(tol/2+20
//            )cover();
//            if(PARTS)board();
//            }
//        if(CUT)cuboid(100,anchor=FACE);
//        }
}    

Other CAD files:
Multimeter/3dp-Files/D1 Mini/Wemos-Mini-D1-ESP32.stl
Multimeter/3dp-Files/Multimeter-Case.stl
Multimeter/3dp-Files/parts/ads1115.stl
Pressure Sensor/3dp-Files/pressureCase.stl
scale/Case.scad
Airquality/3dp/AirQualityCase.scad
Force Sensor/3dp-Files/Archiv/Load_Cell_Hull.scad
Force Sensor/3dp-Files/Archiv/Load_Cell_Hull_lolin.scad
Force Sensor/3dp-Files/Archiv/Load_cell_case_v3.scad
Force Sensor/3dp-Files/Archiv/Load_cell_only_case_v3.scad
Force Sensor/3dp-Files/Archiv/Wagschale.scad
Force Sensor/3dp-Files/Archiv/load_cell_case v4.1.scad
Force Sensor/3dp-Files/Archiv/load_cell_case v4.scad
Force Sensor/3dp-Files/Load_cell_case_v3.scad
Force Sensor/3dp-Files/Load_cell_only_case_v3.scad
Force Sensor/3dp-Files/Wagschale.scad
Force Sensor/3dp-Files/bottom and connector for smaller load cell.stl
Force Sensor/3dp-Files/bottom.stl
Force Sensor/3dp-Files/build_plate.stl
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

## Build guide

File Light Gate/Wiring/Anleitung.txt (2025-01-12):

Benötigte Bauteile:

IR-Geschwindigkeitsmesssensor

IR-LED 5mm
IR-Empfänger Diode 5mm

5mm LED mit Vorwiderstand (z.B. 220 Ohm)

Lolin32Lite

Optional:
Schalter

Lipo-Batterie

RJ45-Breakout Board

Zusamenbau:
Zunächst modifizieren wir den Geschwindigkeitssensor. Auf dem Gehäuse ist markeirt, auf welcher Seite die Infrarot-LED ist. Dies ist teilweise auch auf der Platine gekennzeichnet.
Zunächst wird die schwarze Abdeckung mit einer Zange gelöst, so dass die eingebauten LEDs freiliegen. Diese werden mit einer Kneifzange agetrennt und werden nicht mehr benötigt.

Nun werden an die Lötstellen der Infrarot-LED zwei Kabel von ca. 15 cm länge angelötet (siehe Abbildung). Normalerweise ist der +-Pol beschriftet. Allerdings ist die Beschriftung bei einigen Sensoren fehlerhaft. Also am besten testen, welche Lötstelle die Masse ist.

Analog werden nun die Kabel für den Infrarot-Empfänger angelötet. Bei der Empfänger-Diode ist dir Polarisation genau entgegengesetzt zur LED. Das lange Bein der Diode muss also an den Minus-Pol und das kurze Bein an den Plus-Pol. Normalerweise liegen sich Plus- und Minuspol der Empfänger- und Emitter-Diode genau gegenüber. (Siehe Abbildung)

An die Enden der Kabel werden entsprechend die Dioden angelötet.

Nun empfielt sich ein erster Test, ob der Sensor mit den neuen Dioden funktioniert. Dazu ca. 3.3 V an den Sensor anschließen und testen, ob beim gegenüberhalten der beiden Dioden der Sensor anspricht. Dies wird in der Regel durch die eingebaute LED angezeigt.

Nun wird der Sensor mit dem Lolin32Lite verbunden. VCC kommt an den 3V-Ausgang, GND an GND und der digitale Ausgang des Sensors an den PIN17.

Die Anzeige-LED kann nun noch mit dem Sensor verbunden werden. Dazu wird ein Vorwiderstand an den Plus-Pol der Led angelötet und dieser dann an den digitalen Ausgang des Sensors.
Der Minus-Pol der LED wird mit GND (Sensor oder Lolin32Lite) verbunden.

Soll nur eine Einzellichtschranke gebaut werden, kann jetzt das ganze in das Gehäuse eingebaut werden. 

Für die Doppellichtschranke wird nun noch der RJ45-Adapter angeschlossen.
Dieser versorgt danach die zweite Lichtschranke mit Strom und empfängt gleichzeitig das Signal.

Dazu wird der 3V-Anschluss des Lolin32Lite mit dem Anschluss 2 verbunden, GND mit Anschluss 7. Anschluss 3 wird mit dem PIN 16 des Lolin32Lite verbunden. Hier kommt dann das Signal der zweiten Lichtschranke an. Anschluss 6 wird mit PIN 25 verbunden. Dieser dient dazu, dass beim Start des Sensors erkannt wird, dass eine zweite Lichtschranke angeschlossen ist.

Nun werden die Bauteile an die entsprechnden Stellen im Gehäuse verbaut.

Bau der zweiten Lichtschranke.
Zunächst wird der Geschwindigkeitssensor genau wie der erste mit den (Leucht-)Dioden modifiziert.

Nun muss nur noch der RJ45-Adapter angeschlossen werden.
VCC wird mit Anschluss 2 verbunden, der digitale Ausgang mit Anschluss 3 und GND mit Anschluss 6 UND 7 (kann einfach überbrückt werden)

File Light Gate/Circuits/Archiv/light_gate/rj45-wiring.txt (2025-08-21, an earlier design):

1 				(S3 out electromagnet gelb)
2 V++ rot
3 S2 in weiß
4 Second Light Gate detector				(Button (only magnet) lila)
5
6 
7 GND scwarz
8

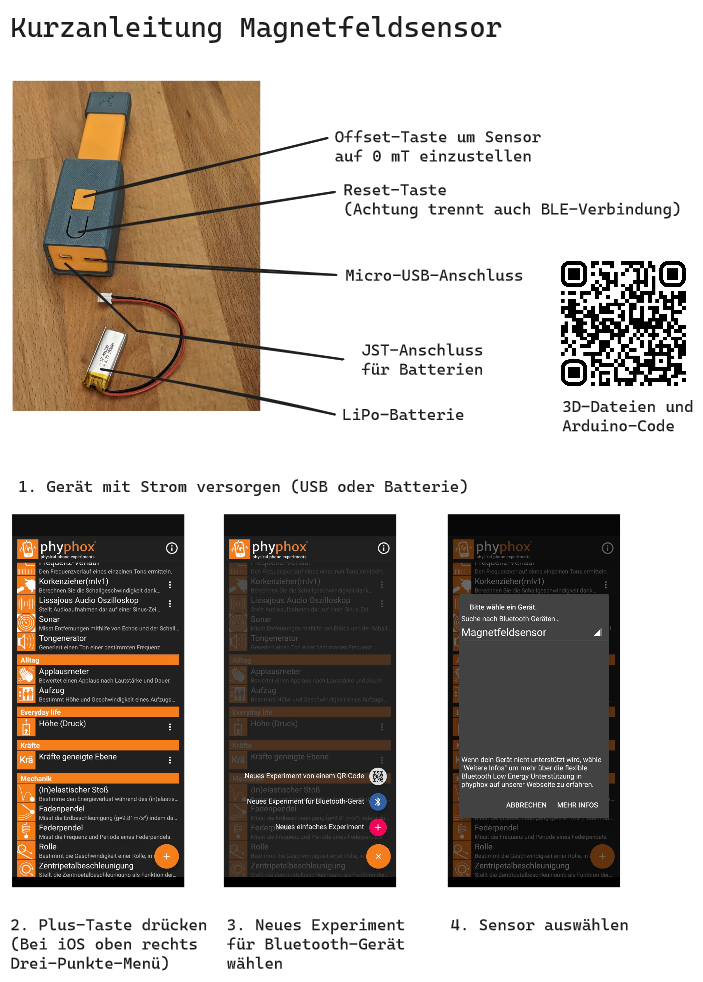
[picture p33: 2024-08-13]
Magnetometer/Pictures/Anleitung.png

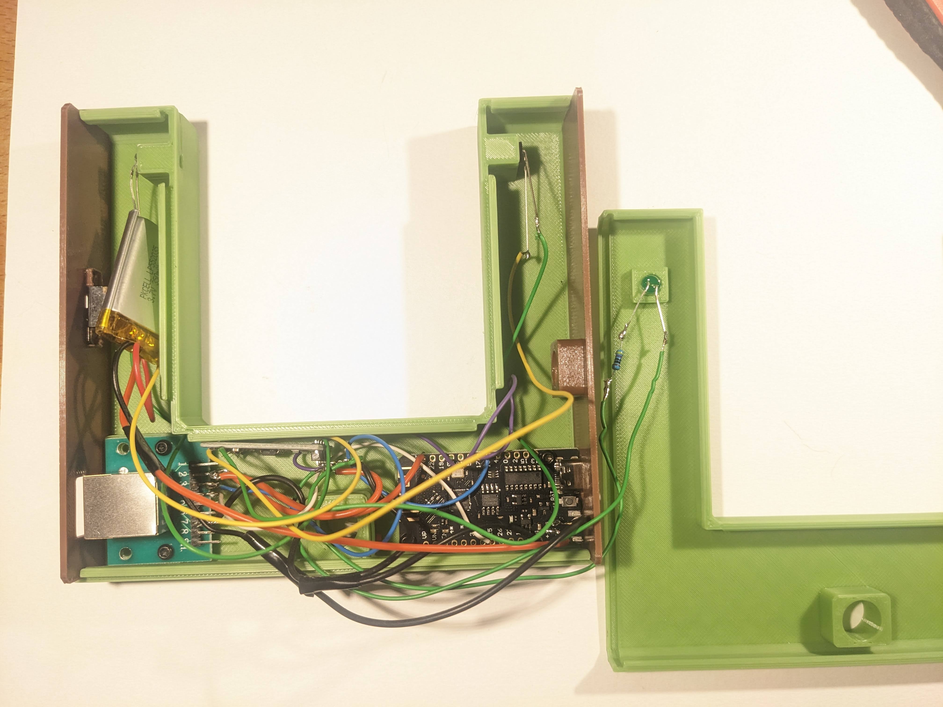
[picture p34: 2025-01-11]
Light Gate/Pictures/Instructions/complete_case.jpg

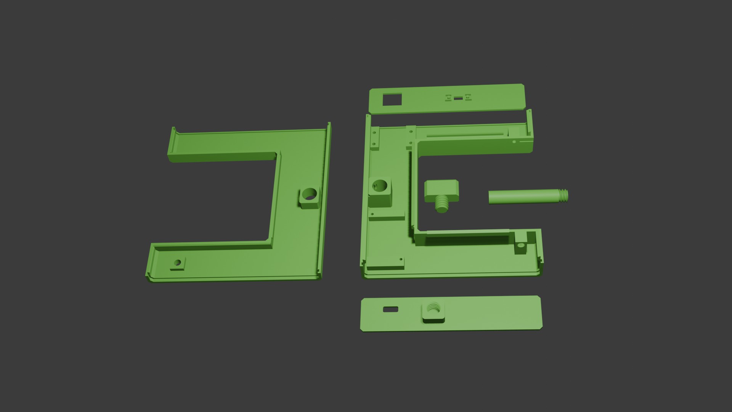
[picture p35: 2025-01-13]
Light Gate/Pictures/Instructions/3dp.jpg

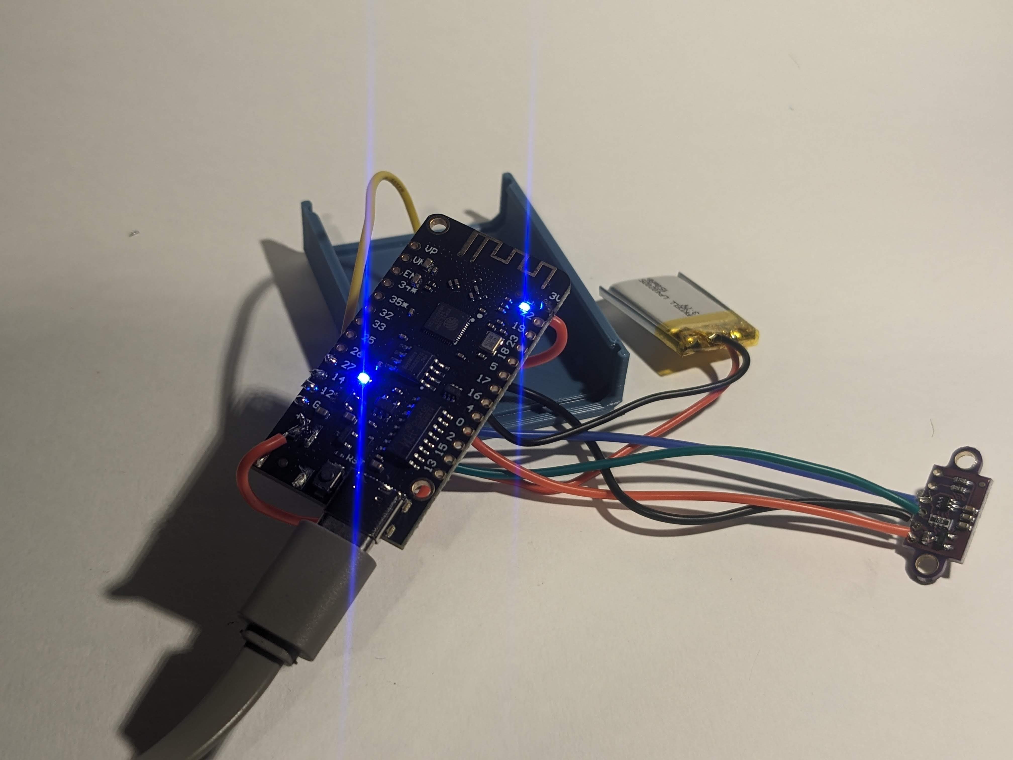
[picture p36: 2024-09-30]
Laser Distance Sensor/Pictures/bauanleitung/tof-workingtest.jpg

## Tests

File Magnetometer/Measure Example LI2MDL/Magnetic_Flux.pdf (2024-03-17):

## Magnetic Flux in long spools

0 | 4 | 8 | 12 | 16

# s in cm

0,00

0,13

0,26

0,39

0,52

0,65

## B in

m

T

N=39; L | =0,1m; I=1,358A

N=100; L=0,15m; I=1,785A

N=19; L =0,08m; I = | | 1,441 | A

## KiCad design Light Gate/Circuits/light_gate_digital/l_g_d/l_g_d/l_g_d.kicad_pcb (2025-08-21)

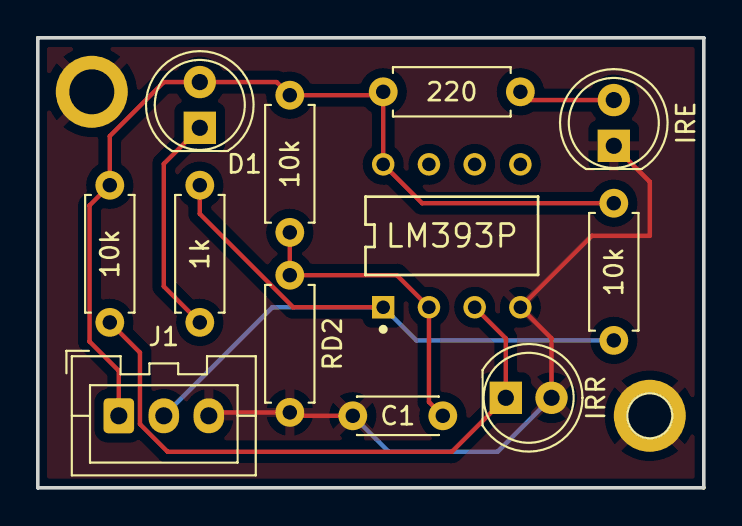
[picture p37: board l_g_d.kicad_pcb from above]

Board: 2 copper layers, 37.0 x 25.0 mm, 12 parts (0 on the bottom side), 7 nets.

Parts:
1k: 1k; R_Axial_DIN0207_L6.3mm_D2.5mm_P7.62mm_Horizontal
10k, 10k#2, 10k#3: 10k; R_Axial_DIN0207_L6.3mm_D2.5mm_P7.62mm_Horizontal
220: 220; R_Axial_DIN0207_L6.3mm_D2.5mm_P7.62mm_Horizontal
C1: C; C_Disc_D4.3mm_W1.9mm_P5.00mm
D1: LED; LED_D5.0mm_IRGrey
IRE: LD271; LED_D5.0mm_IRGrey
IRR: Q_Photo_NPN_CE; LED_D5.0mm_IRGrey
J1: Conn_01x03_Female; JST_XA_B03B-XASK-1_1x03_P2.50mm_Vertical
RD2: 10k; R_Axial_DIN0207_L6.3mm_D2.5mm_P7.62mm_Horizontal
U1: LM393P; Texas_Instruments-P_R-PDIP-T8-0-0-0

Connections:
GND: C1.1, IRE.1 (K), IRR.2 (E), J1.3, RD2.2, U1.4 (GND)
unnamed: 10k.2, C1.2, RD2.1, U1.2 (1IN−)
unnamed: 1k.1, D1.1 (K)
unnamed: 220.2, IRE.2 (A)
unnamed: 1k.2, 10k#2.2, J1.2, U1.1 (1OUT)
unnamed: 10k#3.1, IRR.1 (C), U1.3 (1IN+)
VCC: 10k.1, 10k#2.1, 10k#3.2, 220.1, D1.2 (A), J1.1, U1.8 (VCC)

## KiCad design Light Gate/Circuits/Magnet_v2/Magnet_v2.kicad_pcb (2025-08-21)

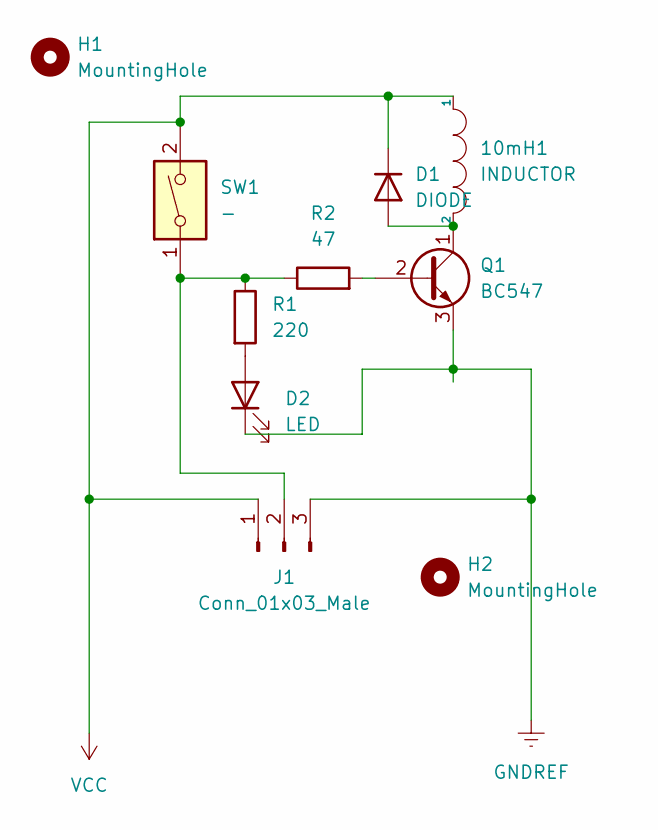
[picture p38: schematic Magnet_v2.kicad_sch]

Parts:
10mH1: INDUCTOR; PinSocket_1x02_P2.54mm_Vertical
D1: DIODE; D_T-1_P10.16mm_Horizontal
D2: LED; LED_D5.0mm
H1, H2: MountingHole; MountingHole_2.5mm
J1: Conn_01x03_Male; PinSocket_1x03_P2.54mm_Vertical
Q1: BC547; TO-92_HandSolder
R1: 220; R_Axial_DIN0207_L6.3mm_D2.5mm_P7.62mm_Horizontal
R2: 47; R_Axial_DIN0207_L6.3mm_D2.5mm_P7.62mm_Horizontal
SW1: -; PinSocket_1x02_P2.54mm_Vertical

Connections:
GNDREF: D2.1 (K), J1.3, Q1.3 (E)
unnamed: 10mH1.2, D1.1 (A), Q1.1 (C)
unnamed: D2.2 (A), R1.2
unnamed: J1.2, R1.1, R2.1, SW1.1
unnamed: Q1.2 (B), R2.2
VCC: 10mH1.1, D1.2 (K), J1.1, SW1.2

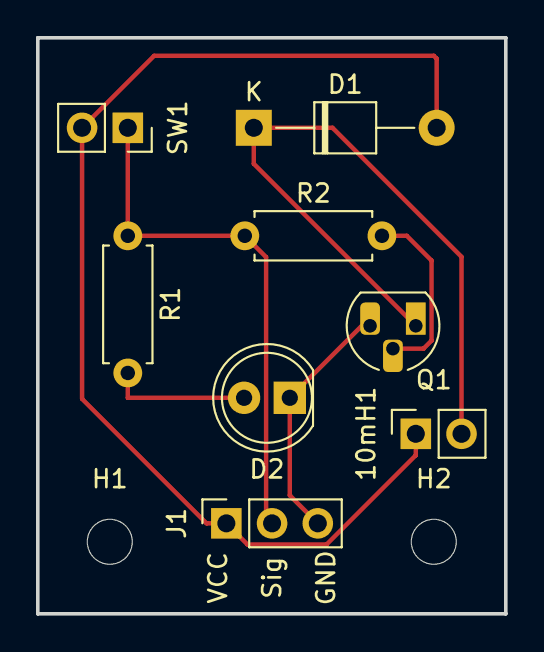
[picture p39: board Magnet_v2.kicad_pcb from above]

Board: 2 copper layers, 26.0 x 32.0 mm, 10 parts (0 on the bottom side), 6 nets.

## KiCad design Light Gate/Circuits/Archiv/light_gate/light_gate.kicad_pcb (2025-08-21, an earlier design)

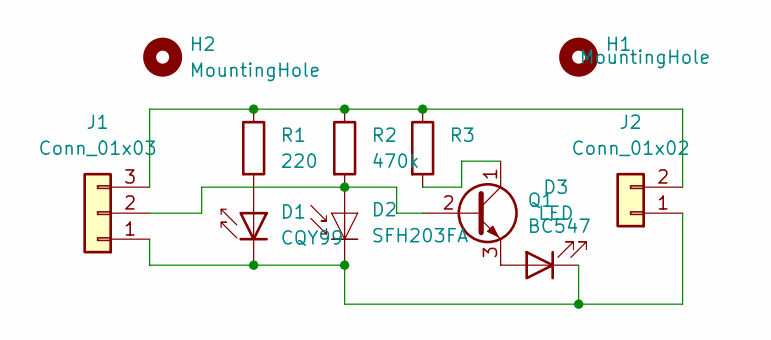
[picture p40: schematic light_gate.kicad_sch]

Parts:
D1: CQY99; LED_D5.0mm_IRGrey
D2: SFH203FA; LED_D5.0mm_IRGrey
D3: LED; LED_D5.0mm
H1, H2: MountingHole; MountingHole_2.2mm_M2_DIN965
J1: Conn_01x03; PinHeader_1x03_P2.54mm_Vertical
J2: Conn_01x02; PinHeader_1x02_P2.54mm_Vertical
Q1: BC547; TO-92L_HandSolder
R1: 220; R_Axial_DIN0207_L6.3mm_D2.5mm_P7.62mm_Horizontal
R2: 470k; R_Axial_DIN0207_L6.3mm_D2.5mm_P7.62mm_Horizontal
R3: R_Axial_DIN0207_L6.3mm_D2.5mm_P7.62mm_Horizontal

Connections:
unnamed: D1.1 (K), D2.1 (K), D3.1 (K), J1.1, J2.1
unnamed: D1.2 (A), R1.2
unnamed: D2.2 (A), J1.2, Q1.2 (B), R2.2
unnamed: D3.2 (A), Q1.3 (E)
unnamed: J1.3, J2.2, R1.1, R2.1, R3.1
unnamed: Q1.1 (C), R3.2

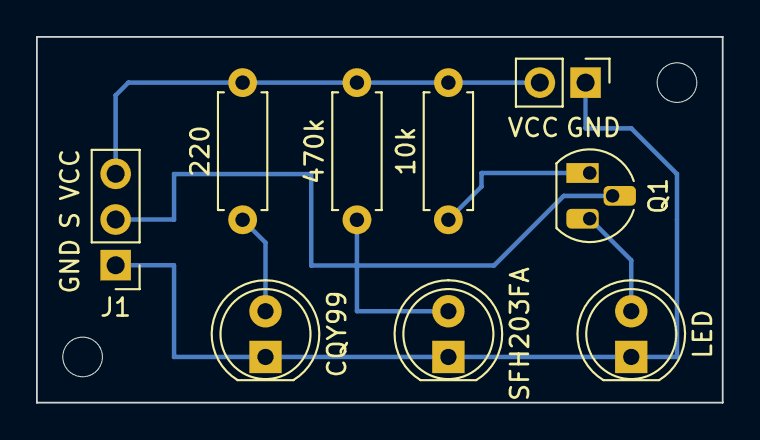
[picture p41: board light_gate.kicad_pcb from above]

Board: 2 copper layers, 38.1 x 20.3 mm, 11 parts (0 on the bottom side), 6 nets.

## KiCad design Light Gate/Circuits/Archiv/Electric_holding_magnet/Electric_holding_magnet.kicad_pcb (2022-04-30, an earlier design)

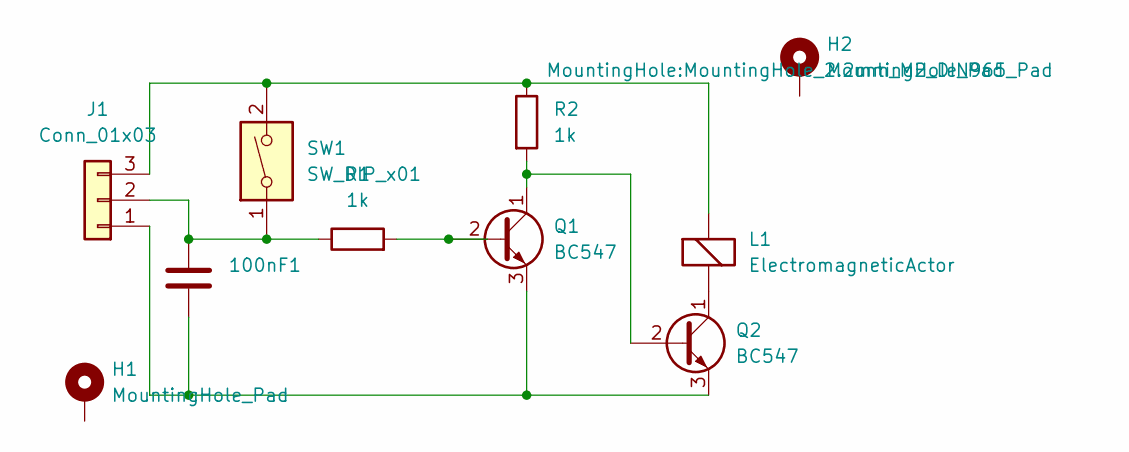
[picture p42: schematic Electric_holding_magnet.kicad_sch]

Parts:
100nF1: (no value)
H1, H2: MountingHole_Pad; MountingHole_2.2mm_M2_DIN965_Pad
J1: Conn_01x03; PinHeader_1x03_P2.54mm_Vertical
L1: ElectromagneticActor; PinHeader_1x02_P2.54mm_Vertical
Q1, Q2: BC547; TO-92_HandSolder
R1, R2: 1k; R_Axial_DIN0207_L6.3mm_D2.5mm_P7.62mm_Horizontal
SW1: SW_DIP_x01; PinHeader_1x02_P2.54mm_Vertical

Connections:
unnamed 0: 100nF1.2, J1.1, Q1.3 (E), Q2.3 (E); also elsewhere on the board
unnamed 1: 100nF1.1, J1.2, R1.1, SW1.1; also elsewhere on the board
unnamed: J1.3, L1.1 (-), R2.1, SW1.2
unnamed: L1.2 (+), Q2.1 (C)
unnamed: Q1.1 (C), Q2.2 (B), R2.2
unnamed: Q1.2 (B), R1.2

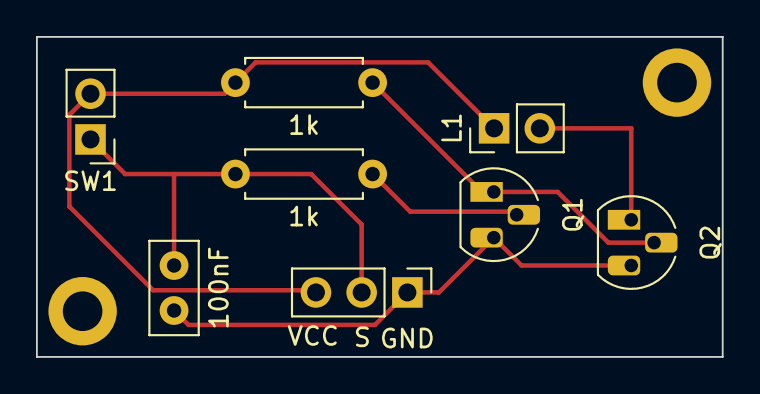
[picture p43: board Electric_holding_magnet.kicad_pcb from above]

Board: 2 copper layers, 38.1 x 17.8 mm, 10 parts (0 on the bottom side), 6 nets.

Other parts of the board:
100nF: C; C_Disc_D5.0mm_W2.5mm_P2.50mm

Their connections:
unnamed 0: 100nF.2; also elsewhere on the board
unnamed 1: 100nF.1; also elsewhere on the board

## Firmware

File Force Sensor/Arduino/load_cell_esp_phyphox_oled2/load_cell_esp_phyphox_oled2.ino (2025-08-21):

#include <HX711_ADC.h>
#include <phyphoxBle.h>
#include <Adafruit_GFX.h>
#include <Adafruit_SSD1306.h>

#define BUTTON_PIN 2 
#define SCREEN_WIDTH 128 // OLED display width, in pixels
#define SCREEN_HEIGHT 32 // OLED display height, in pixels

#define OLED_RESET     -1 // Reset pin # (or -1 if sharing Arduino reset pin)
#define SCREEN_ADDRESS 0x3C ///< See datasheet for Address; 0x3D for 128x64, 0x3C for 128x32
Adafruit_SSD1306 display(SCREEN_WIDTH, SCREEN_HEIGHT, &Wire, OLED_RESET);

HX711_ADC LoadCell(4, 5); //LoadCell(DT,SCK)
HX711_ADC LoadCell2(33,14);

//calibration factor for primary load cell
const float calFactor = 1066.4;

//calibration factor for secondary load cell (connected via rj45)
const float calFactor2 = 1019.34;

int tara = 0;
int reset = 0;
float t_offset = 0;

void setup() {
  Wire.begin(32,33);//SDA SCL
  //Turn on the internal LED on lolin 32
  pinMode(LED_BUILTIN, OUTPUT);
  digitalWrite(LED_BUILTIN, LOW);
  
  PhyphoxBLE::start("Kraftsensor C");
     // PhyphoxBLE::configHandler = &receivedData;
  PhyphoxBLE::experimentEventHandler = &newExperimentEvent;
  PhyphoxBLE::printXML(&Serial);

  PhyphoxBleExperiment kraft; 
  //
  kraft.setTitle("Kraftsensor");
  kraft.setCategory("Sensor-Boxen");
  
 //View
  PhyphoxBleExperiment::View firstView;
  firstView.setLabel("Graph"); //Create a "view"
  PhyphoxBleExperiment::View secondView;
  secondView.setLabel("Einfach"); //Create a "view"
  PhyphoxBleExperiment::View waage;
  waage.setLabel("Waage");
  PhyphoxBleExperiment::View dual;
  dual.setLabel("Zwei Sensoren");
  

  //
  PhyphoxBleExperiment::Graph firstGraph;      //Create graph which will p lot random numbers over time     
  firstGraph.setLabel("Kraft");
  firstGraph.setUnitX("s");
  firstGraph.setUnitY("N");
  firstGraph.setLabelX("Zeit t");
  firstGraph.setLabelY("Kraft F");

  firstGraph.setChannel(1,2);

  PhyphoxBleExperiment::Graph secondGraph;      //Create graph which will p lot random numbers over time     
  secondGraph.setLabel("Kraft");
  secondGraph.setUnitX("s");
  secondGraph.setUnitY("N");
  secondGraph.setLabelX("Zeit t");
  secondGraph.setLabelY("Kraft F_2");

  secondGraph.setChannel(1,4);

  //Value
  PhyphoxBleExperiment::Value force;         //Creates a value-box.
  force.setLabel("F");                  //Sets the label
  force.setPrecision(3);                     //The amount of digits shown after the decimal point.
  force.setUnit("N");                        //The physical unit associated with the displayed value.
  force.setColor("FFFFFF");                  //Sets font color. Uses a 6 digit hexadecimal value in "quotation marks".
  force.setChannel(2);
  force.setXMLAttribute("size=\"2\"");

  PhyphoxBleExperiment::Value mass;         //Creates a value-box.
  mass.setLabel("m");                  //Sets the label
  mass.setPrecision(1);                     //The amount of digits shown after the decimal point.
  mass.setUnit("g");                        //The physical unit associated with the displayed value.
  mass.setColor("FFFFFF");                  //Sets font color. Uses a 6 digit hexadecimal value in "quotation marks".
  mass.setChannel(3);
  mass.setXMLAttribute("size=\"2\"");

  //Value
  PhyphoxBleExperiment::Value force2;         //Creates a value-box.
  force2.setLabel("F_2");                  //Sets the label
  force2.setPrecision(3);                     //The amount of digits shown after the decimal point.
  force2.setUnit("N");                        //The physical unit associated with the displayed value.
  force2.setColor("FFFFFF");                  //Sets font color. Uses a 6 digit hexadecimal value in "quotation marks".
  force2.setChannel(4);
  force2.setXMLAttribute("size=\"2\"");

  PhyphoxBleExperiment::Value mass2;         //Creates a value-box.
  mass2.setLabel("m_2");                  //Sets the label
  mass2.setPrecision(1);                     //The amount of digits shown after the decimal point.
  mass2.setUnit("g");                        //The physical unit associated with the displayed value.
  mass2.setColor("FFFFFF");                  //Sets font color. Uses a 6 digit hexadecimal value in "quotation marks".
  mass2.setChannel(5);
  mass2.setXMLAttribute("size=\"2\"");


  firstView.addElement(force);
  firstView.addElement(firstGraph); 
  secondView.addElement(force);
  waage.addElement(mass);
  dual.addElement(firstGraph);
  dual.addElement(force);
  dual.addElement(secondGraph);
  dual.addElement(force2);
  kraft.addView(firstView);
  kraft.addView(secondView);
  kraft.addView(waage);
  kraft.addView(dual);
  
  PhyphoxBLE::addExperiment(kraft);
   
  LoadCell.begin(); // start connection to HX711
  LoadCell.start(2000); // load cells gets 2000ms of time to stabilize
  LoadCell.setCalFactor(calFactor); 

  LoadCell2.begin(); // start connection to HX711
  LoadCell2.start(2000); // load cells gets 2000ms of time to stabilize
  LoadCell2.setCalFactor(calFactor2); 
  
  
  Serial.begin(115200); 
  pinMode(BUTTON_PIN, INPUT_PULLUP);

  
  if(!display.begin(SSD1306_SWITCHCAPVCC, 0x3C)) { // Address 0x3D for 128x64
    Serial.println(F("SSD1306 allocation failed"));
    for(;;);
  }
  //delay(2000);
  display.clearDisplay();
  display.setRotation(2);
  display.setTextSize(1);
  display.setTextColor(WHITE);
  display.setCursor(0, 10);
  // Display static text
  display.println("Start");
  display.display(); 
  delay(500);

}



void loop() {
   int buttonState = digitalRead(BUTTON_PIN);

  
  if(!buttonState){
    Serial.println("press");
    LoadCell.tareNoDelay();
    LoadCell2.tareNoDelay();
    while(tara == 0){
      LoadCell.update();
      tara = LoadCell.getTareStatus();
    };
    tara = 0;
  }
  static boolean newDataReady = 0;
  if (LoadCell.update()) newDataReady = true;
  LoadCell2.update();

  if (newDataReady && reset == false) {

  float t = 0.001 * ((float)millis() - t_offset);
  float incDat = LoadCell.getData();
  float m = abs(incDat);
  float f = incDat *9.81/1000;
  float incDat2 = LoadCell2.getData();
  float m2 = abs(incDat2);
  float f2 = -incDat2 *9.81/1000;
  PhyphoxBLE::write(t,f,m,f2,m2);

  display.clearDisplay();
  display.setTextSize(2);
  display.setCursor(10,0);
  display.print(f);
  display.setCursor(80,0);
  display.print('N');
  display.setCursor(10,15);
  display.print(m,1);
  display.setCursor(80,15);
  display.print('g');
  display.display();

  Serial.print("t(s)");Serial.print(",");Serial.print(t);Serial.print(",");
  Serial.print("F(N)");Serial.print(",");Serial.print(f,3);Serial.print(",");
  Serial.print("m(g)");Serial.print(",");Serial.print(m,1);Serial.print(",");
  Serial.print("F2(N)");Serial.print(",");Serial.print(f2,3);Serial.print(",");
  Serial.print("m2(g)");Serial.print(",");Serial.println(m2,1);//Serial.print(touchValue);
  newDataReady = false;
  }

}

void newExperimentEvent(){
  if(PhyphoxBLE::eventType==1 && reset){
    t_offset = (float)millis();
    reset = false;
  }
  if(PhyphoxBLE::eventType == 2){
    t_offset = (float)millis();
    reset = true;
  }
}

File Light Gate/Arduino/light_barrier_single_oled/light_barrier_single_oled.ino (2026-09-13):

/*
 * Title: Einzellichtschranke
 * Version: 1.01
 * Author: Heinrich Lauterbach
 * GitHub: https://github.com/HeiLaut/ble-physics-sensors
 *
 * License (own code): MIT License
 *
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
 * Libraries used:
 * - phyphoxBLE (LGPL 3.0) - https://github.com/phyphox/phyphox-arduino
 * - Adafruit_GFX (BSD License) - https://github.com/adafruit/Adafruit-GFX-Library
 * - Adafruit_SSD1306 (BSD License) - https://github.com/adafruit/Adafruit_SSD1306
 */


#include <phyphoxBle.h>
#include <Wire.h>
#include <Adafruit_GFX.h>
#include <Adafruit_SSD1306.h>

// ---- Pin-Konfiguration ----
#define SIGNAL_PIN 26  
#define BUTTON_PIN 27
#define SDA_PIN 16   
#define SCL_PIN 17
#define LED_PIN 32
// ---- OLED ----
#define SCREEN_WIDTH 128
#define SCREEN_HEIGHT 32
#define NAME "Einzel-Lichtschranke A"

Adafruit_SSD1306 oled(SCREEN_WIDTH, SCREEN_HEIGHT, &Wire, -1);

volatile int n = 0;
volatile int t1 = 0;
volatile int t2 = 0;
volatile int timeArray[3] = {0, 0, 0};
volatile float laufT = 0;
volatile float pendelT = 0;
volatile float pendelF = 0;
volatile bool newEvent = false;
volatile unsigned long lastRise = 0;
const unsigned long DEBOUNCE_US = 2000; // Startwert, ggf. anpassen

float verdT = 0;
int n_puffer = 0;
bool stopped = 0;
bool cleared = 0;
bool synced = 0;

volatile float t = 0;
volatile float t_offset = 0;
// ---- Mode/Taster ----
// 0 = Laufzeit, 1 = Verdunklung, 2 = Pendel

int mode = 0;
bool lastButtonState = HIGH;   


void IRAM_ATTR isr1() {
  n++;
  if (digitalRead(SIGNAL_PIN)) {
    unsigned long now = micros();
    if (now - lastRise < DEBOUNCE_US) return;  // Prellen ignorieren, timeArray NICHT verschieben
    lastRise = now;
    t1 = (int)now;
    timeArray[0] = timeArray[1];
    timeArray[1] = timeArray[2];
    timeArray[2] = t1;
    newEvent = true;

  } else {
    t2 = (int)micros();

  }

}

void setup() {
  PhyphoxBLE::start(NAME);
  PhyphoxBLE::setMTU(48); //6 float values 6*4 = 24 bytes
  
  xTaskCreate(
    generateExperiment,
    "experimentTask",
    16000,
    NULL,
    1,
    NULL
  );

  PhyphoxBLE::experimentEventHandler = &newExperimentEvent;

  Serial.begin(115200);

  Wire.begin(SDA_PIN, SCL_PIN);
  if (!oled.begin(SSD1306_SWITCHCAPVCC, 0x3C)) {
    Serial.println(F("failed to start SSD1306 OLED"));
    while (1);
  }

  pinMode(SIGNAL_PIN, INPUT_PULLUP);
  pinMode(BUTTON_PIN, INPUT_PULLUP);
  pinMode(LED_PIN, OUTPUT);
  attachInterrupt(digitalPinToInterrupt(SIGNAL_PIN), isr1, CHANGE);

  t_offset = 0;

  pinMode(LED_BUILTIN, OUTPUT);
  digitalWrite(LED_BUILTIN, LOW);

}

void loop() {
  if (digitalRead(SIGNAL_PIN)) {
    digitalWrite(LED_PIN, LOW);  
  }else{
    digitalWrite(LED_PIN,HIGH);

  }
  bool reading = digitalRead(BUTTON_PIN);

  if (reading == LOW && lastButtonState == HIGH) {
    mode++;
    mode %= 4;
    delay(50);
    //Serial.println("press");
   }

  lastButtonState = reading;


  if(digitalRead(SIGNAL_PIN)){
    verdT = abs((float)t1 - (float)t2) * 0.000001f;
  }
  // Measures the time between t1 and the last two rising timestamps
 

 if (newEvent) {

    newEvent = false;
    t  = 0.000001f * (float)t1 - t_offset;
    laufT   = (timeArray[2] - timeArray[1]) * 0.000001f;
    pendelT = (timeArray[2] - timeArray[0]) * 0.000001f;
    pendelF = 1.0f / pendelT;

    float values[6] = {t,laufT,verdT,pendelT,pendelF,(float)floor(n/2)};
    PhyphoxBLE::write(&values[0], 6);
    Serial.print("t,");Serial.print(t,3);
    Serial.print(",Laufzeit,");Serial.print(laufT,3);
    Serial.print(",Verdunklungszeit,"); Serial.print(verdT,4);
    Serial.print(",Schwingungsdauer,");Serial.print(pendelT,3);
    Serial.print(",Frequenz,");Serial.print(pendelF,3);
    Serial.print(",n,");Serial.println(floor(n/2),0);
  }
  n_puffer = n;

  // ---- OLED-Ausgabe ----
  oled.clearDisplay();
  oled.setTextColor(WHITE);

  if(mode == 0){
    oled.setTextSize(1);
    oled.setCursor(5,0);  oled.print("Laufzeit");
    oled.setTextSize(2);
    oled.setCursor(5,10); oled.print(laufT,3); oled.print(" s");
  }
  if(mode == 1){
    oled.setTextSize(1);
    oled.setCursor(5,0);  oled.print("Verdunklung");
    oled.setTextSize(2);
    oled.setCursor(5,10); oled.print(verdT,4); oled.print(" s");
  }
  if(mode == 2){
    oled.setTextSize(1);
    oled.setCursor(5,0);  oled.print("Pendel T");
    oled.setTextSize(2);
    oled.setCursor(5,10); oled.print(pendelT,3); oled.print(" s");
  }
   if(mode == 3){
    oled.setTextSize(1);
    oled.setCursor(5,0);  oled.print("Pendel f");
    oled.setTextSize(2);
    oled.setCursor(5,10); oled.print(pendelF,3); oled.print(" Hz");
  }


  oled.setTextSize(1);
  oled.setCursor(120,0);
  oled.print(mode);
  oled.display();

  //delay(50);
}

void generateExperiment(void * parameter) {
  PhyphoxBleExperiment lightBarrier;

  lightBarrier.setTitle("Einzel-Lichtschranke");
  lightBarrier.setCategory("Sensor-Boxen");
  lightBarrier.numberOfChannels = 6;
  lightBarrier.setDescription("Lichtschranke");

  PhyphoxBleExperiment::View graph;
  graph.setLabel("Vielfachmessung");

  PhyphoxBleExperiment::View simple;
  simple.setLabel("Laufzeiten");

  PhyphoxBleExperiment::View multi;
  multi.setLabel("Pendel");

  PhyphoxBleExperiment::Graph nGraph;
  nGraph.setLabel("Ereignisse");
  nGraph.setUnitY("");
  nGraph.setUnitX("s");
  nGraph.setLabelX("Zeit t");
  nGraph.setLabelY("");
  nGraph.setColor("FFCC5C");
  nGraph.setChannel(1,6);

  PhyphoxBleExperiment::Value verd;
  verd.setLabel("Verd.zeit t =");
  verd.setPrecision(4);
  verd.setUnit("s");
  verd.setColor("FFCC5C");
  verd.setChannel(3);
  verd.setXMLAttribute("size=\"2\"");

  PhyphoxBleExperiment::Graph verdGraph;
  verdGraph.setLabel("Verd.zeit");
  verdGraph.setUnitY("s");
  verdGraph.setUnitX("s");
  verdGraph.setLabelX("t");
  verdGraph.setLabelY("dT");
  verdGraph.setStyle(STYLE_DOTS);
  verdGraph.setLinewidth(2);
  verdGraph.setColor("76a5af");
  verdGraph.setChannel(1,3);

  PhyphoxBleExperiment::Value laufz;
  laufz.setLabel("Laufzeit t =");
  laufz.setPrecision(3);
  laufz.setUnit("s");
  laufz.setColor("FFCC5C");
  laufz.setChannel(2);
  laufz.setXMLAttribute("size=\"2\"");

  PhyphoxBleExperiment::Value schwingd;
  schwingd.setLabel("Schw.dauer T =");
  schwingd.setPrecision(3);
  schwingd.setUnit("s");
  schwingd.setColor("FFCC5C");
  schwingd.setChannel(4);
  schwingd.setXMLAttribute("size=\"2\"");

  PhyphoxBleExperiment::Value freq;
  freq.setLabel("Frequenz f =");
  freq.setPrecision(3);
  freq.setUnit("Hz");
  freq.setColor("FFCC5C");
  freq.setChannel(5);
  freq.setXMLAttribute("size=\"2\"");

  PhyphoxBleExperiment::Graph periodGraph;
  periodGraph.setLabel("Schwingungsdauer");
  periodGraph.setUnitY("s");
  periodGraph.setUnitX("");
  periodGraph.setLabelX("n");
  periodGraph.setLabelY("T");
  periodGraph.setStyle(STYLE_DOTS);
  periodGraph.setLinewidth(2);
  periodGraph.setColor("76a5af");
  periodGraph.setChannel(6, 4);

  simple.addElement(verd);
  simple.addElement(laufz);

  graph.addElement(verdGraph);
  graph.addElement(nGraph);

  multi.addElement(schwingd);
  multi.addElement(freq);
  multi.addElement(periodGraph);

  lightBarrier.addView(simple);
  lightBarrier.addView(multi);
  lightBarrier.addView(graph);

  PhyphoxBLE::addExperiment(lightBarrier);

  vTaskDelete(NULL);
}


void newExperimentEvent(){
 
  if(PhyphoxBLE::eventType==1){
    Serial.println("Start");
    if(cleared){
      t_offset = 0.000001f * (float)micros();
      n = 0;
      n_puffer = 0;
    }
    stopped = 0;
    cleared = 0;
  }

  if(PhyphoxBLE::eventType==2){
    Serial.println("Clear");
    stopped = 1;
    synced  = 1;
    cleared = 1;
  }

  if(PhyphoxBLE::eventType==255){
    stopped = 1;
    synced  = 1;
    cleared = 1;
    Serial.println("synced");
  }
}

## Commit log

2022-03-04 added space for esp32 d1 in lid
    [Load_Cell_Hull.scad, Load_Cell_Hull_lid.stl, esp32.stl]
2022-03-04 change port
    [Load_Cell_Hull.scad, Load_Cell_Hull_lid.stl]
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2022-03-05 changed tolerances in load cell hull
    [Load_Cell_Hull.scad, Load_Cell_Hull_lid.stl]
2022-03-05 Update Load_Cell_Hull.scad
    changed lid
    [Load_Cell_Hull.scad]
2022-03-07 redesign load_cell_hull
    [Load_Cell_Hull.scad]
2022-03-08 tuning hull
    [Load_Cell_Hull.scad, Load_Cell_Hull.stl]
2022-03-08 work on stl
    [Load_Cell_Hull.scad, Load_Cell_Hull.stl, Load_Cell_Hull_lid.stl]
2022-03-09 finalize hull for force
    [Load_Cell_Hull.scad, Load_Cell_Hull.stl, Load_Cell_Hull_inner.stl]
2022-03-09 added photos, tweak ino for force
    [Load_Cell_Hull.scad, Load_Cell_Hull.stl, Load_Cell_Hull_inner.stl, Load_Cell_all.stl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]
2022-03-09 edit lid
    [Load_Cell_Hull.scad, Load_Cell_all.stl, Load_Cell_lid.stl]
2022-03-10 added ultrasonic and voltmeter files
    [HC-SR04.stl, Load_Cell_Hull.scad, Load_Cell_all.stl, Load_Cell_box.stl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]
2022-03-10 updatet mount for ultrasonic sensor box
    [huelle_us.scad, huelle_us.stl]
2022-03-10 added circuits
    [Arduino_nano.scad, Arduino_nano_box.scad, Arduino_nano_box.stl, HC-SR04.stl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]
2022-03-11 change serial rate
    [Arduino_nano.scad, Arduino_nano_box.scad, Arduino_nano_box.stl]
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2022-03-14 changed 3dp file
    [huelle_us.scad, huelle_us.stl, ultrasonic esp32 mini case .stl]
2022-03-15 ToF laser
    Added ToF-Laser 3dp files and first ino
    [VL53L0X.stl, esp32.stl, hull.scad, hull.stl]
2022-03-15 changed tof tolerances
    [Load_Cell_Hull.scad, hull.scad, hull.stl]
2022-03-16 changed button hole
    [hull.scad, hull.stl]
2022-03-17 added circuit
    [circuit.fzz]
2022-03-17 changed fritzing
    [circuit.fzz]
2022-03-18 changed lid
    now lid can be screwed
    [huelle_us.scad, huelle_us.stl]
2022-03-18 changed lid parameters
    [huelle_us.scad]
2022-03-24 created voltmeter box for esp32
    [voltmeter_box_esp32.scad, voltmeter_box_esp32.stl]
2022-03-24 change ino to measure correct voltage
    [esp input problem.xlsx]
2022-03-31 added files
    added files for the light barrier and the case for the esp32 - same as the voltmeter case
    [case.scad, case.stl, esp32_case.scad, esp32_case.stl]
2022-03-31 updated case
    [case.scad, case.stl]
2022-03-31 Create Unbenannt 1.ods
    [Unbenannt 1.ods]
2022-04-03 changed clearance
    [case.scad, case.stl]
2022-04-07 Create light barrier.fzz
    [light barrier.fzz]
2022-04-07 createt case for magnet starter
    [starter-case.scad, starter-case.stl]
2022-04-07 created new case with esp
    [case_with_lolin.scad, case_with_lolin.stl, lolin.stl]
2022-04-19 added case with din
    [case_with_din.stl, case_with_lolin.scad, case_with_lolin.stl, case_with_lolin_lid.stl]
2022-04-19 added kicad files
    [Electric_holding_magnet-B_Cu.gbr, Electric_holding_magnet-B_Mask.gbr, Electric_holding_magnet-B_Paste.gbr, Electric_holding_magnet-B_Silkscreen.gbr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]
2022-04-21 added circuit for ina219
    [ina219.kicad_pcb, ina219.kicad_sch]
2022-04-21 added multimter print files
    [esp32.stl, ina219_h.stl, multimeter.scad, multimeter.stl]
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2022-04-21 added new version of case
    [case_v2.scad]
2022-04-28 removed stl files
    [esp32_case.scad, esp32_case.stl, lid_esp.stl, lolin.stl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]
2022-04-28 removed files, not needed
    [case.stl, case_with_din.stl, case_with_lolin.stl]
2022-04-28 removed files not needed
    [case_with_lolin.scad, case_with_lolin_lid.stl]
2022-04-28 udated footprints npn
    [light_gate.kicad_pcb, light_gate.kicad_sch]
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2022-04-28 updated files
    [multimeter_d1_mini.scad, multimeter_lolin_lite.scad]
2022-04-30 update pnp footprint
    [Electric_holding_magnet.kicad_pcb, Electric_holding_magnet.kicad_sch]
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2022-05-20 added lolin 32 case
    [multimeter_lolin_lite.scad, multimeter_lolin_lite.stl]
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2022-05-20 added case files
    [barometer-case.scad, barometer-case.stl, bmp180.stl]
2022-06-21 activate i2c ports for lolin lite
    [Wagschale.scad]
2022-09-04 new file for lolin32
    [Load_Cell_Hull_lolin.scad]
2022-09-04 new lolin case files
    [tof_lolin_lite.scad, tof_lolin_lite.stl]
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2022-10-05 changed case
    [Load_Cell_Hull.scad, Load_Cell_Hull_lolin.scad, Load_Cell_all.stl, Load_Cell_box.stl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]
2022-10-05 changed circuit
    [Magnet_v2-B_Cu.gbr, Magnet_v2-B_Mask.gbr, Magnet_v2-B_Paste.gbr, Magnet_v2-B_Silkscreen.gbr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]
2022-10-05 added thermosensor
    [Thermosensor.scad, Thermosensor.stl, jst.stl]
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2022-11-17 added lm393 to lightgate
    [Magnet_v2.kicad_sch, l_g_d-B_Cu.gbr, l_g_d-B_Mask.gbr, l_g_d-B_Paste.gbr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]
2023-01-21 added simple r-speed-sensor
    [OLED.stl, case.scad, case.stl, mh-sensor.stl]
2023-01-21 small design changes
    [case_v2.scad]
2023-01-21 added complete new case
    [keystone.stl, load_cell_case v4.1.scad, load_cell_case v4.1.stl, load_cell_case v4.1_lid.stl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]
2023-03-07 added lb case
    [case_v2.stl]
2023-04-20 Change the folder structure
    [Electric_holding_magnet-B_Cu.gbr, Electric_holding_magnet-B_Mask.gbr, Electric_holding_magnet-B_Paste.gbr, Electric_holding_magnet-B_Silkscreen.gbr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]
2023-04-20 changed folder names
    [Electric_holding_magnet-B_Cu.gbr, Electric_holding_magnet-B_Mask.gbr, Electric_holding_magnet-B_Paste.gbr, Electric_holding_magnet-B_Silkscreen.gbr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]
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2024-01-29 new case
    added files for a completely new case design, moved old design in sepreate folder
    [TactSwitch.stl, VL53L0X.stl, VL53L1X.stl, esp32.stl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]
2024-01-29 moved old files to archive
    [light barrier.fzz]
2024-02-17 add case2 library file
    [Case2.scad]
2024-02-17 reorgenized files
    [Speichenrad.scad, Speichenrad.stl, Speichenrad20.stl, Speichenrad_30.stl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]
2024-02-28 updatet light gate and messwagen 3dp files
    [Messwagen.scad, Messwagen.stl]
2024-03-17 new sensor
    added new arduino sketch fpr mlx90393
    added case files for the sensor
    add readme for the case files
    created stl files
    [Bottom_Case_Lolin32Lite.stl, Magnetometer-Case.scad, Magnetometer-Case_v2.scad, Magnetometer-Case_v2.stl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]
2024-03-17 bluedot_case
    added bluedot case files
    [VL53L1X_bluedot.stl, vl53l1x_case2_bluetdot_vl53l1x.scad, vl53l1x_case2_bluetdot_vl53l1x.stl]
2024-03-17 changed a lot
    [Messwagen.stl, Messwagen_diy_LG.scad, Messwagen_diy_LG.stl, Messwagen_diy_double light_gate.stl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]
2024-03-20 case update
    complete update of the case. moved the old files in the archive
    [Button.stl, CaseV3.stl, LeftPanel_Button.stl, LeftPanel_Keystone_RJ45.stl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]
2024-03-20 minor changes
    [Magnetometer-Case_v2.scad]
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2024-04-03 add usb-c variant
    [LightGateCasev3.scad]
2024-04-07 updated mounting possibilities
    [Bottom.stl, Encoder_Wheel.scad, Encoder_Wheel.stl, LightGateCasev3.scad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]
2024-04-08 moved to athciv
    [LightGateCasev3.scad]
2024-04-08 re arrange
    moved old to archiv, add new fil
    [Multimeter-Case.scad, Multimeter-Case.stl, Top_with_holes.stl, esp32.stl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]
2024-04-08 changed resistor
    [Electric_holding_magnet-B_Cu.gbr, Electric_holding_magnet-B_Mask.gbr, Electric_holding_magnet-B_Paste.gbr, Electric_holding_magnet-B_Silkscreen.gbr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]
2024-04-08 changed screwtype
    [Encoder_Wheel.scad, wheel.stl]
2024-04-08 add fritzing files
    [INA.fzz, LightGate.fzz, LightGate_single.fzz]
2024-06-11 file order
    [Messwagen.scad, Messwagen.stl, Messwagen_diy_LG.scad, Messwagen_diy_LG.stl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]
2024-06-11 deleted dublicates
    [doppellichtschranke.scad, doppellichtschranke.stl, encoder_adapter.stl, encoder_rad.scad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]
2024-08-13 update case and code
    [Case.scad, Case_Vl53l0X_Plate.stl, Encoder_Wheel.scad, Encoder_Wheel.stl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]
2024-08-15 udpate wiring and remove old files
    [Case2.scad, INA.fzz, LightGate_single.fzz, Load_cell_case_v3.scad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]
2024-09-07 update case
    [vl53l0x_case2.scad, vl53l0x_case2.stl]
2024-09-15 update force sensor case
    [case_v5.scad, case_v5.stl, case_v5_bottom_wo.stl, case_v5_empty.stl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]
2024-09-30 update cases and sketches
    [Encoder_Wheel.scad, Encoder_Wheel.stl, Force.fzz, Kugelstarter.scad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]
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2024-10-08 new Sensor
    [AirQualityCase.scad, AirQualityCase.stl]
2024-10-08 update wiring diagram
    [Force.fzz]
2024-10-08 update case with embossing
    [vl53l0x_case2.stl]
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2024-10-14 add space for temperaturesensor
    [AirQualityCase.scad, AirQualityCase.stl]
2025-01-13 add buildplate light gate
    [ALL_PARTS.stl]
2025-03-17 added switch position indicator
    [Case_Vl53l0X_Plate.stl, Multimeter-Case.scad, Multimeter-Case.stl]
2025-03-17 update several parts and intro text
    [Case2.scad]
2025-03-18 sorting
    update licence and minor adjustments to the files
    [00_BUILD_PLATE.stl, Case_build_plate.stl, LightGateCasev3_1_rj45.scad, Magnetometer-Case_v2.scad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]
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2025-03-21 added pin names
    [Force.fzz]
2025-08-21 update oled
    [case_v5.scad, oled_case.scad, plate_oled.stl]
2025-08-23 update to usb-c
    [case_v5.scad, panel_usbC_switch.stl]
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
